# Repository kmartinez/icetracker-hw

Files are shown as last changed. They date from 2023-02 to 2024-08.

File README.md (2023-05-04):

# GDP Glacier Monitor

## Name
GDP Glacier Monitor - Hardware - part of the glacsweb.org project at The University of Southampton

## File Info
```
├── GlacTracker_PSU_V1
│   ├── GlacTracker_PSU.brd - EAGLE board file
│   ├── GlacTracker_PSU.sch - EAGLE schematic file
│   ├── GlacTracker_PSU_BOM.xlsx - Overall BOM
│   ├── mgc1g18_GlacTracker_PSU.zip - Gerber Files
│   ├── mgc1g18_GlacTracker_PSU_JLC_bom.xls - BOM for JLC pick and place
│   ├── mgc1g18_GlacTracker_PSU_top_cpl.csv - CPL for JLC pick and place
├── GlacTrackerMCU_V1 
│   ├── GlacTracker.brd - EAGLE board file
│   ├── GlacTracker.sch - EAGLE schematic file
│   ├── mgc1g18_GlacTrackerMCU.zip - Gerber Files
├── GlacTrackerMCU_V2
│   ├── GlacTracker.brd - EAGLE board file
│   ├── GlacTracker.sch - EAGLE schematic file
├── GlacTracker7 - an Eagle7 respin of the separate PSU and MCU boards into a single board
│   ├── tracker.brd - EAGLE board file
│   ├── tracker.sch - EAGLE schematic file
```

### GlacTracker3
This is in IT3 (IceTracker3) and will be the second deployed system in Iceland in 2023.
It has a simplified PSU: 3.3V and 4V with added FET switches to control power to various modules.
The GSM and SWARM are swappable and only one can be installed (to avoid issues with UARTS and we only need one)
It relies on several commercial boards: thing+, sparkfun ublox m9 GPS, sparkfun SWARM, Adafruit SD and Ardusimple's version of Xbee radio.

## GlacTracker_PSU
GlacTracker_PSU designed first to provide 3 configurable supplies through the MP2155 switching regulators. As well as a connection to the "battery" (the output of the BQ24074 Li-Ion battery Charger)
* The default settings are:
    * 3.3V
    * VCC_1 (set to 3.3V) with an optional 3.3V LDO which can be enabled by setting VCC_1 to around 4V (by changing resistor values) and connecting jumpers.
    * 5V
    * V_GSM - connection to the "battery" as described above

Each of these supplies can be enabled or disabled through both on board jumpers and via an external 6-way JST connector meaning when all supplies are disabled the leakage current is very low.

After testing it was found that using the V_GSM connector to power the GSM module was not viable as it cannot operate on voltages below 3.3V. Given this system uses Li-Ion batteries that can go as low as 2.8V, this was not a viable option.

Instead VCC_1 was set to 4V by changing R8 to 120k and two 470uF capacitors were added to the V_BAT input on the GSM module to handle current spikes during transmission. This means GSM can be used in all battery charge states.

* The current supply is setup as follows:
    * 3.3V - used to power MCU, GPS and radio. Enabled via RTC alarm enable circuit
    * VCC_1 - set to 4V used to power GSM. Enabled by MCU on demand
    * 5V - used to power SWARM. Enabled by MCU on demand
    * V_GSM - NO LONGER USED TO POWER GSM, when enabled can be used to read V_BAT

### Changes for V2
* V_GSM is now redundant as is being powered through 4V supply
* LDO is not being used to can be removed

# GlacTrackerMCU
This is the the "MCU" board with the MCU, GPS, Radio, GSM & SWARM.

The hardware is the same for a base station and rover, however the GSM & SWARM modules are not fitted on the rovers.

### GlacTrackerMCU_V2
Contains minor changes from V1 that were discovered after V1 had been "ordered":
* Capacitors added to V_BAT pin of GSM
* Diode removed from PSU_EN as not required.

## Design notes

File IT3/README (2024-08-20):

this is the final PCB design used in 2023/4

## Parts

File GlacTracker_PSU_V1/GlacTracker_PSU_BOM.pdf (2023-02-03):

Designator | Quantity Value | Footprint | Manufacture Part # | Supplier Part # | Description
C1,C6,C11 | 3 DNF | | | | SMD Capacitor
C10 | 1 22pF | 0603 | 0603CG220J500NT | JLC: C91701 | SMD Capacitor
C16,C17,C18 | 3 1uF | 0805 | 0805B105K500NT | JLC: C215803 | SMD Capacitor
C19,C20 | 2 4.7uF | 0805 | 0805X475K500CT | JLC: C296082 | SMD Capacitor
C2,C7,C12 | 3 10uF | 0805 | 0805B106K100NT | JLC: C90544 | SMD Capacitor
C3,C4,C8,C9,C13,C14 | 6 22uF | 0805 | 0805X226M100NT | JLC: C503482 | SMD Capacitor
C5,C15 | 2 68pF | 0603 | 06035A680JAT2A | JLC: C210002 | LED Red
LED1,LED2 | 2 | SML0805 | D-R080508L3-KS2 | JLC: C130114 | P-Channel 30V 5A 1.3V @ 250uA 47mΩ @ 5A,10V 2W
Q1 | 1 | TSOP-6 | AO6401A | JLC: C102604 | MOSFET N Trench 60V 4.1A 3V @ 250uA 85 mΩ @ 2.5A,10V
Q2 | 1 | SOT-89-3 | DMN6070SY-13 | JLC: C129583 | 100mW 50V ±100ppm/℃ ±1% -55℃~+155℃
R1,R4,R7 | 3 820k | 0603 | RS-03K8203FT | JLC: C322006 | 100mW Thick Film Resistors 75V ±100ppm/℃ ±1% -55℃~+155℃
R11,R13 | 2 4.7k | 0603 | 0603WAF4701T5E | JLC: C23162 | 100mW Thick Film Resistors 75V ±100ppm/℃ ±1% -55℃~+155℃
R12 | 1 1.1k | 0603 | 0603WAF1101T5E | JLC: C22764 | 100mW Thick Film Resistors 75V ±100ppm/℃ ±1% -55℃~+155℃
R14,R15 | 2 1.5k | 0603 | 0603WAF1501T5E | JLC: C22843 | 100mW Thick Film Resistors 75V ±100ppm/℃ ±1% -55℃~+155℃
R16,R17 | 2 10k | 0603 | 0603WAF1002T5E | JLC: C25804 | 100mW Thick Film Resistors 50V ±100ppm/℃ ±1% -55℃~+125℃
R2,R8 | 2 143k | 0603 | CR0603FA1433G | JLC: C100772 | 100mW Thick Film Resistors 75V ±100ppm/℃ ±1% -55℃~+155℃
R3,R9 | 2 750k | 0603 | 0603WAF7503T5E | JLC: C23240 | 100mW Thick Film Resistors 75V ±100ppm/℃ ±1% -55℃~+155℃
R5 | 1 91k | 0603 | 0603WAF9102T5E | JLC: C23265 | 100mW Thick Film Resistors 150V ±100ppm/℃ ±1% -55℃~+155℃
R6 | 1 681k | 0603 | ERJ3EKF6813V | JLC: C403328 | 100mW Thick Film Resistors 75V ±100ppm/℃ ±1% -55℃~+155℃
U1,U2,U3 | 3 MP2155GQ-Z | QFN-10_MP2155_MNP MP2155GQ-Z | JLC: C110397 | QFN-10_3x3x05P DC-DC Converter
U4 | 1 3.3V | SOT23-5 | AP2112K-3.3TRG1 | JLC: C51118 | Fixed 3.3V LDO
U5 | 1 BQ24074QFN_3X3 QFN_3X3 | BQ24074RGTR | JLC: C54313 | Battery Management IC
F1 | 1 | 1812 | MF-MSMF200-2 | RS: 647-8263 | 2A/8V PPTC Fuse
J1,J2,J3,J4,J5,J7,J8 | 7 | | S2B-PH-SM4-TB | RS: 688-1353 | JST 2MM MALE RA CONNECTOR
J6 | 1 | | SM06B-SRSS-TB | RS: 546-8827 | JST 6 pin vertical connector
L1,L2,L3 | 3 | 7050 | 744314330 | RS: 736-1951 | Shielded Wire-wound SMD Inductor

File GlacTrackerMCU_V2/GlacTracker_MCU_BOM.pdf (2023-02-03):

Designator | Quantity | Value | Footprint | Description
BT1 | | 3000TR | BAT_3000TR | Ultra Low Profile SMT Coin Cell Battery Contact Retainer for 12 mm Cell
C1, C2, C3, C4, C6, C8 | | 100n | 0603 | Capacitor - Generic
C5 | | 1uF | 0603 | Capacitor - Generic
C7 | | 100pf | 0603 | Capacitor - Generic
C9, C10 | | 470uF | TH | Capacitor Polarised - Generic
J1 | SPARKFUN-SAMD51-THINGPLUS TH
J2, J3, J4 | | | JST-2-SMD | JST 2MM MALE RA CONNECTOR
J5 | JST_6_PIN_VERTICAL | JST-6-SMD-VERT-1.0MM JST 6 pin vertical connector
LED1, LED2, LED3 | | | CHIP-LED0805 | LED
Q1 | | 2N3906 | TO92 | PNP Transistor
R1, R2 | | 100k | 0603 | Generic Resistor Package
R3, R4, R5 | | 1k | 0603 | Generic Resistor Package
U1 | | DS3231-BREAKOUT | TH
U2 | | FONA-800-BREAKOUT | TH
U4 | | SPARKFUN-SWARM-M138 | TH
U5 | | SPARKFUN-GPS-ZED-F9P | TH
XB1 | | XBEE-SX868 | TH | XBee(TM)/XBee-PRO(TM) ZB SMT RF Modules.

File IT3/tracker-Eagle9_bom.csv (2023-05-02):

Comment | Designator | Footprint | LCSC Part #
 | 3.3V | CHIP-LED0805 | C142303
 | 4.4V | CHIP-LED0805 | C142303
 | GPS | CHIP-LED0805 | C142303
 | GSM | CHIP-LED0805 | C142303
 | JP1 | JP1
 | JP2 | JP1
 | JP3 | JP1
 | JP5 | JP1
 | LED_EN | JP1
 | LED4 | SML0805 | C142303
 | LED5 | SML0805 | C142303
820k | R6 | 0603
845k | R9 | 0603
1.1k | R14 | 0603
1.5k | R16 R17 | 0603
1k | R3 R4 R5 R27 | 0603
1uF | C21 | C0805
1uF | C5 | CAPC1608X85 | C105524
1uF | C23 | CAPC2012X110 | C318694
2A/16V | F1 | F1812 | C70126
2N3906 | Q1 | TO92
3.3uH | L1 L3 | WE-HCI_7050
4.7k | R13 R15 | 0603
4.7uF | C24 C25 | CAPC2012X110 | C730468
10k | R23 R28 | 0603
10uF | C12 C17 | CAPC2012X110 | C162430
22-23-2021 | SOLAR | 22-23-2021
22uF | C13 C14 C18 C19 | CAPC2012X110 | C77074
68pF | C15 C20 | CAPC1608X85 | C779986
100k | R1 R2 R18 R19 R20 R21 R22 | 0603
100n | C1 C2 C3 C4 C6 C8 | CAPC1608X85 | C913910
100pf | C7 | CAPC1608X85 | C307357
143k | R7 | 0603
121k | R10 | 0603
340K 0.1% | R25 | R0805 | C865414
470uF | C9 C10 | CAPPRD508W65D1000H1100B
680K 0.1% | R24 | R0805 | C445667
750k | R8 R11 | 0603
3000TR | BT1 | BAT_3000TR | C964830
ADAFRUIT-XTSD | U$1 | ADAFRUIT-XTSD
ADXL343BCCZ-RL7 | U1 | PQFN80P300X500X100-14N
BQ24074QFN_3X3 | U8 | QFN_3X3 | C54313
DMG6602SVT | Q2 Q3 Q7 | TSOT26 | C110497
DNF | C11 C16 | CAPC2012X110
DNF | R12 | P640
DNP | R26 | 0603
DS3231SN | U7 | SOIC127P1032X265-16N
FONA-800-BREAKOUTNOHOLE | U2 | FONA-800-BREAKOUT-NH
JUMPER-SMT_2_NC_TRACE_SILK | JP4 JP10 | SMT-JUMPER_2_NC_TRACE_SILK
MMBT3906LT1SMD | Q6 | SOT23-BEC | C53444
MP2155GQ-Z | U3 U6 | QFN-10_MP2155_MNP
SLOT130.5 | U$2 | SLOT130.5
SPARKFUN-GPS-ZED-F9P | U5 | SPARKFUN-GPS-ZED-F9P
SPARKFUN-SWARM-M138NOTOPHOLE | U4 | SPARKFUN-SWARM-M138-NTH
TEST-POINTTP_15TH_THRU | TP1 TP3 TP6 | TP_15TH
THING_PLUS_PHYSICAL | J1 | THING_PLUS
XBEE-PRO | XB1 | XBEE-PRO
XT30PW-M | BAT | XT30PW-M

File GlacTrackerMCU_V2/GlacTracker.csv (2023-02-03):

Part | Value | Device | Package | Description | AVAILABILITY | CATEGORY | DESCRIPTION | MANUFACTURER | MF | MP | MPN | OPERATING_TEMP | PACKAGE | PART_STATUS | POPULARITY | PRICE | PROD_ID | PURCHASE-URL | ROHS_COMPLIANT | SERIES | SF_ID | SUB-CATEGORY | THERMALLOSS | TP_SIGNAL_NAME | TYPE | VALUE | VOLTAGE_RATING
BT1 | 3000TR | 3000TR | BAT_3000TR | Ultra Low Profile SMT Coin Cell Battery Contact Retainer for 12 mm Cell Check availability | In Stock |  | SMT Holder for 12mm Cell-Tin Nickel Plate on T&R |  | Keystone | 3000TR |  |  | None |  |  | None |  | https://pricing.snapeda.com/search/part/3000TR/?ref=eda
C1 | 100n | C_CHIP-0603(1608-METRIC) | CAPC1608X85 | Capacitor - Generic |  | Capacitor
C2 | 100n | C_CHIP-0603(1608-METRIC) | CAPC1608X85 | Capacitor - Generic |  | Capacitor
C3 | 100n | C_CHIP-0603(1608-METRIC) | CAPC1608X85 | Capacitor - Generic |  | Capacitor
C4 | 100n | C_CHIP-0603(1608-METRIC) | CAPC1608X85 | Capacitor - Generic |  | Capacitor
C5 | 1uF | C_CHIP-0603(1608-METRIC) | CAPC1608X85 | Capacitor - Generic |  | Capacitor
C6 | 100n | C_CHIP-0603(1608-METRIC) | CAPC1608X85 | Capacitor - Generic |  | Capacitor
C7 | 100pf | C_CHIP-0603(1608-METRIC) | CAPC1608X85 | Capacitor - Generic |  | Capacitor
C8 | 100n | C_CHIP-0603(1608-METRIC) | CAPC1608X85 | Capacitor - Generic |  | Capacitor
C9 | 470uF | C-POL_RADIAL-11MM-DIA | CAPPRD508W65D1000H1100B | Capacitor Polarised - Generic |  | Capacitor
C10 | 470uF | C-POL_RADIAL-11MM-DIA | CAPPRD508W65D1000H1100B | Capacitor Polarised - Generic |  | Capacitor
J1 | THING_PLUS_PHYSICAL | THING_PLUS_PHYSICAL | THING_PLUS
J2 |  | JST_2MM_MALE | JST-2-SMD | JST 2MM MALE RA CONNECTOR |  |  |  |  |  |  |  |  |  |  |  |  | CONN-11443 |  |  |  | PRT-08612
J3 |  | JST_2MM_MALE | JST-2-SMD | JST 2MM MALE RA CONNECTOR |  |  |  |  |  |  |  |  |  |  |  |  | CONN-11443 |  |  |  | PRT-08612
J4 |  | JST_2MM_MALE | JST-2-SMD | JST 2MM MALE RA CONNECTOR |  |  |  |  |  |  |  |  |  |  |  |  | CONN-11443 |  |  |  | PRT-08612
J5 | JST_6_PIN_VERTICAL | JST_6_PIN_VERTICAL | JST-6-SMD-VERT-1.0MM | JST 6 pin vertical connector |  |  |  |  |  |  |  |  |  |  |  |  | CONN-08249 |  |  |  | GPS-00579
JP1 | JUMPER-SMT_2_NC_TRACE_SILK | JUMPER-SMT_2_NC_TRACE_SILK | SMT-JUMPER_2_NC_TRACE_SILK | Normally closed trace jumper
JP2 | JUMPER-SMT_2_NC_TRACE_SILK | JUMPER-SMT_2_NC_TRACE_SILK | SMT-JUMPER_2_NC_TRACE_SILK | Normally closed trace jumper
JP3 | JUMPER-SMT_2_NC_TRACE_SILK | JUMPER-SMT_2_NC_TRACE_SILK | SMT-JUMPER_2_NC_TRACE_SILK | Normally closed trace jumper
LED1 |  | LEDCHIP-LED0805 | CHIP-LED0805 | LED |  |  |  |  |  |  |  |  |  |  | 68
LED2 |  | LEDCHIP-LED0805 | CHIP-LED0805 | LED |  |  |  |  |  |  |  |  |  |  | 68
LED3 |  | LEDCHIP-LED0805 | CHIP-LED0805 | LED |  |  |  |  |  |  |  |  |  |  | 68
Q1 | 2N3906 | 2N3906 | TO92 | PNP Transistor |  |  |  |  |  |  |  |  |  |  | 11
R1 | 100k | RESISTOR0603 | 0603 | Generic Resistor Package
R2 | 100k | RESISTOR0603 | 0603 | Generic Resistor Package
R3 | 1k | RESISTOR0603 | 0603 | Generic Resistor Package
R4 | 1k | RESISTOR0603 | 0603 | Generic Resistor Package
R5 | 1k | RESISTOR0603 | 0603 | Generic Resistor Package
TP1 | TP2P2-38-17 | TP2P2-38-17 | P2-38-17 | Test pad |  |  |  |  |  |  |  |  |  |  | 0
TP2 | TP2P2-38-17 | TP2P2-38-17 | P2-38-17 | Test pad |  |  |  |  |  |  |  |  |  |  | 0
TP3 | TP2P2-38-17 | TP2P2-38-17 | P2-38-17 | Test pad |  |  |  |  |  |  |  |  |  |  | 0
U1 | DS3231-BREAKOUT | DS3231-BREAKOUT | DS3231-BREAKOUT
U2 | FONA-800-BREAKOUT | FONA-800-BREAKOUT | FONA-800-BREAKOUT
U4 | SPARKFUN-SWARM-M138 | SPARKFUN-SWARM-M138 | SPARKFUN-SWARM-M138
U5 | SPARKFUN-GPS-ZED-F9P | SPARKFUN-GPS-ZED-F9P | SPARKFUN-GPS-ZED-F9P
XB1 | XBEE-SMT | XBEE-SMT | XBEE-SMT | XBee(TM)/XBee-PRO(TM) ZB SMT RF Modules.

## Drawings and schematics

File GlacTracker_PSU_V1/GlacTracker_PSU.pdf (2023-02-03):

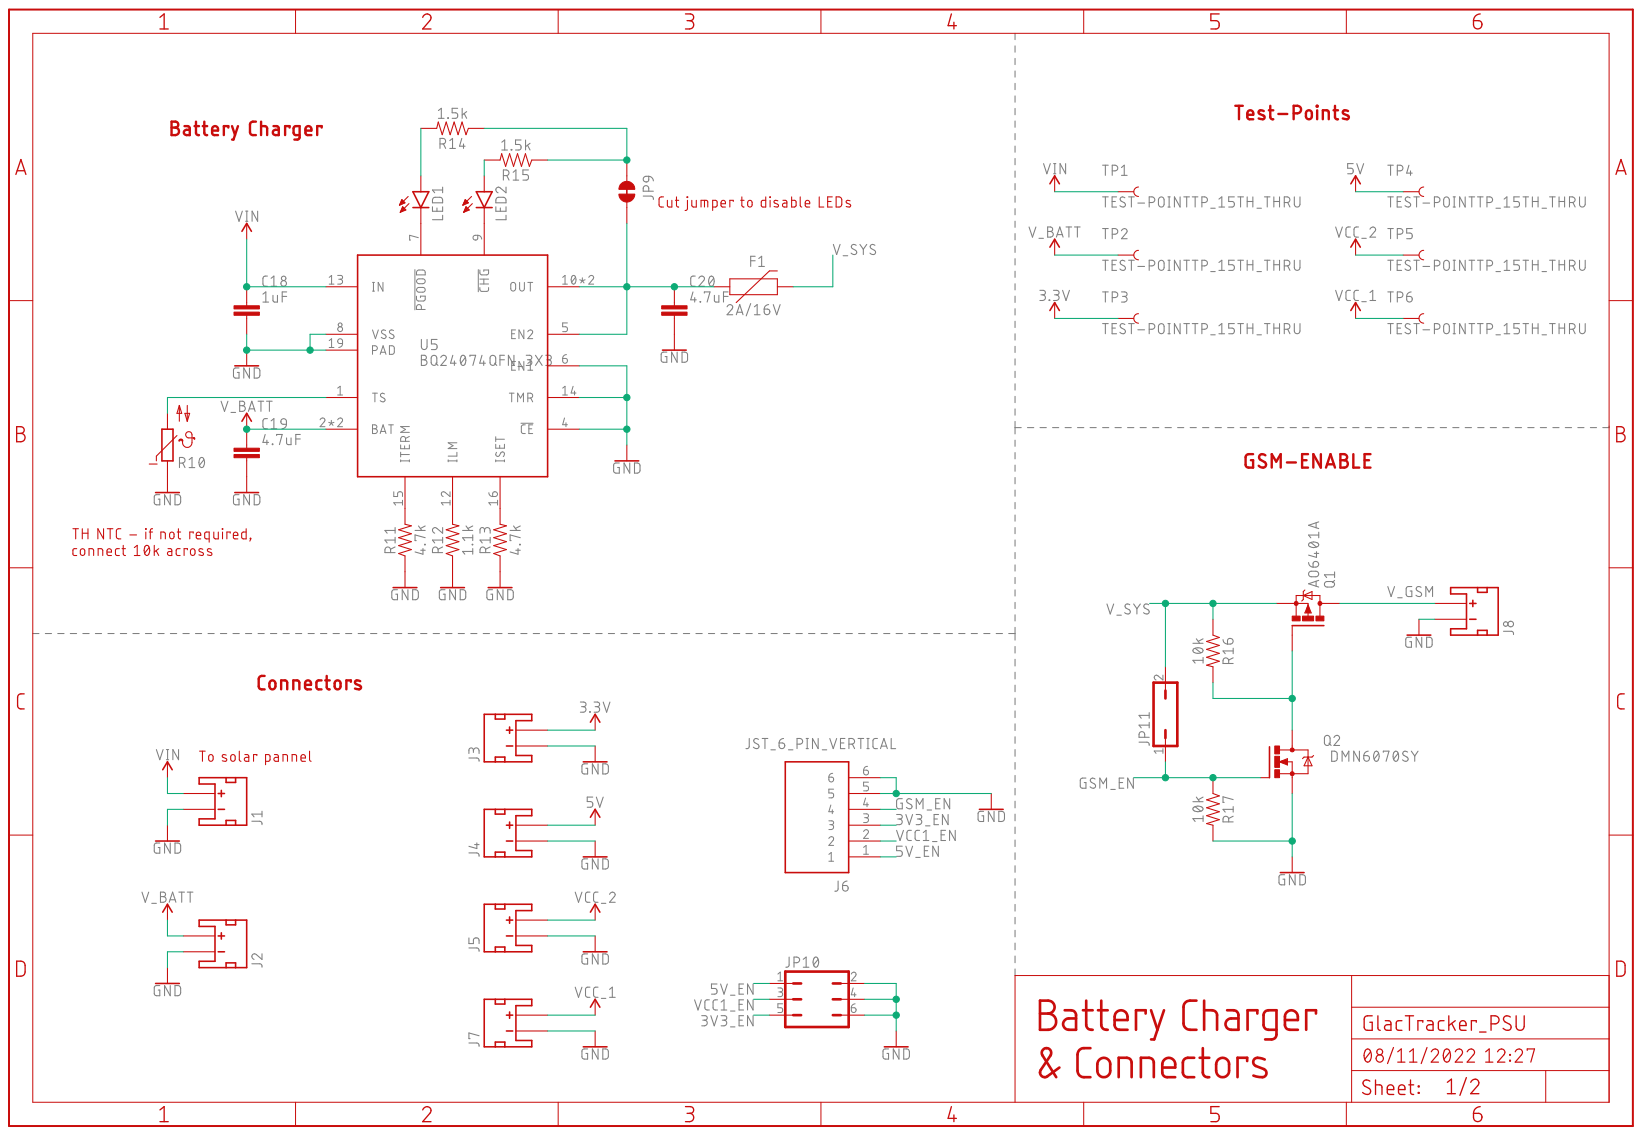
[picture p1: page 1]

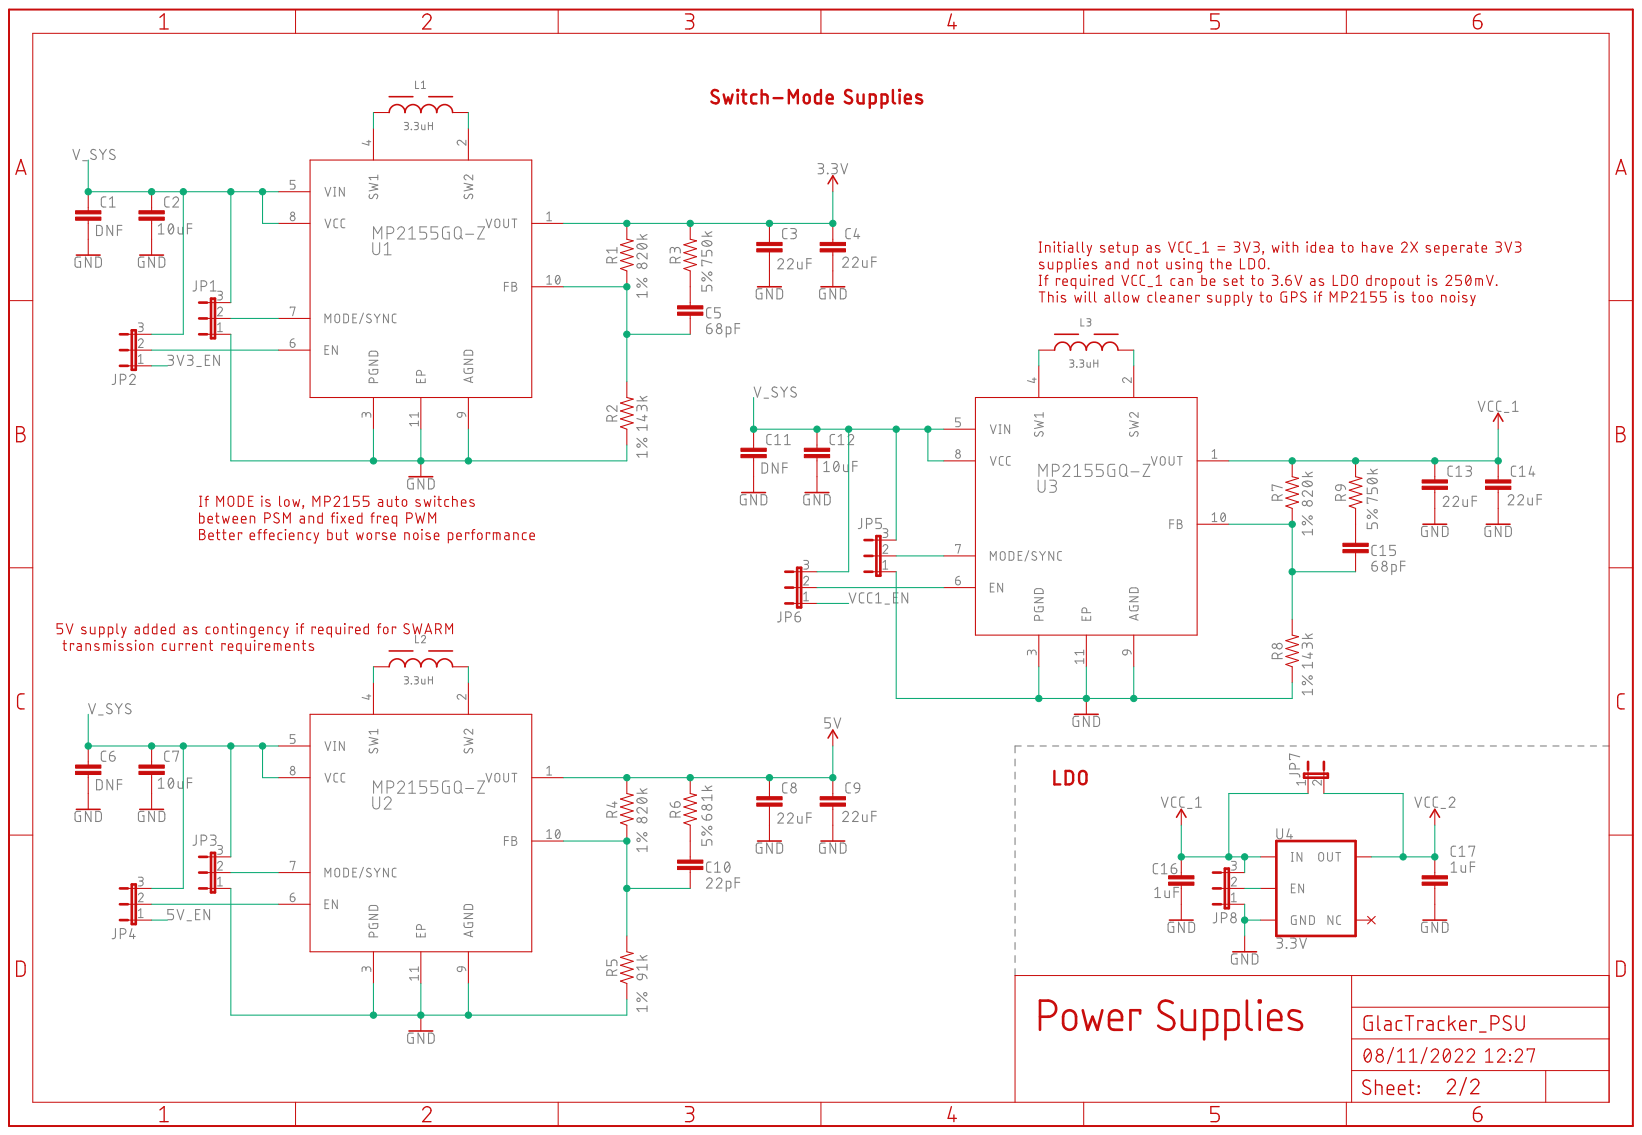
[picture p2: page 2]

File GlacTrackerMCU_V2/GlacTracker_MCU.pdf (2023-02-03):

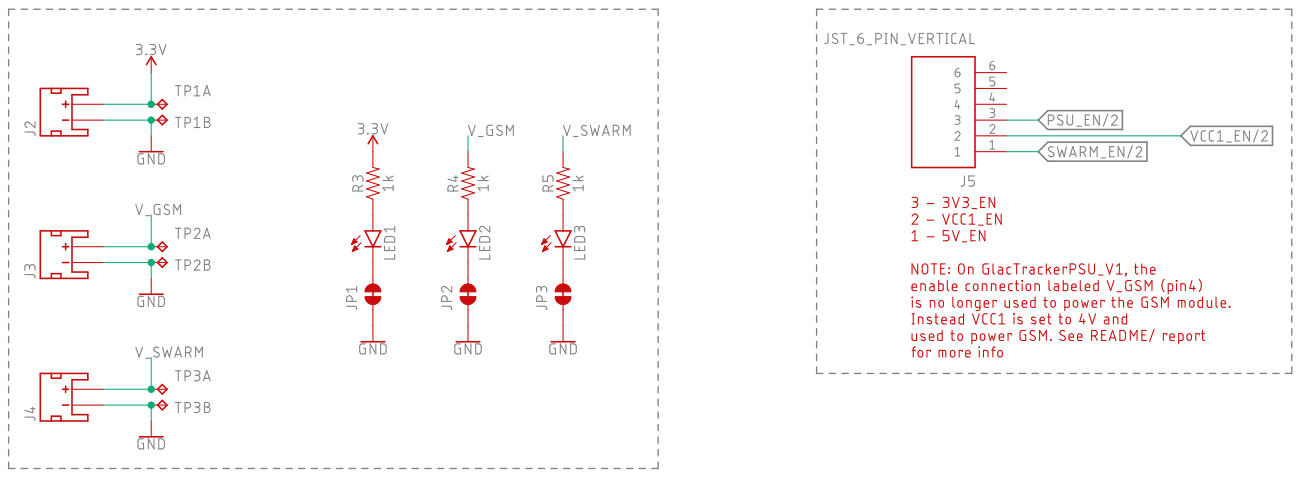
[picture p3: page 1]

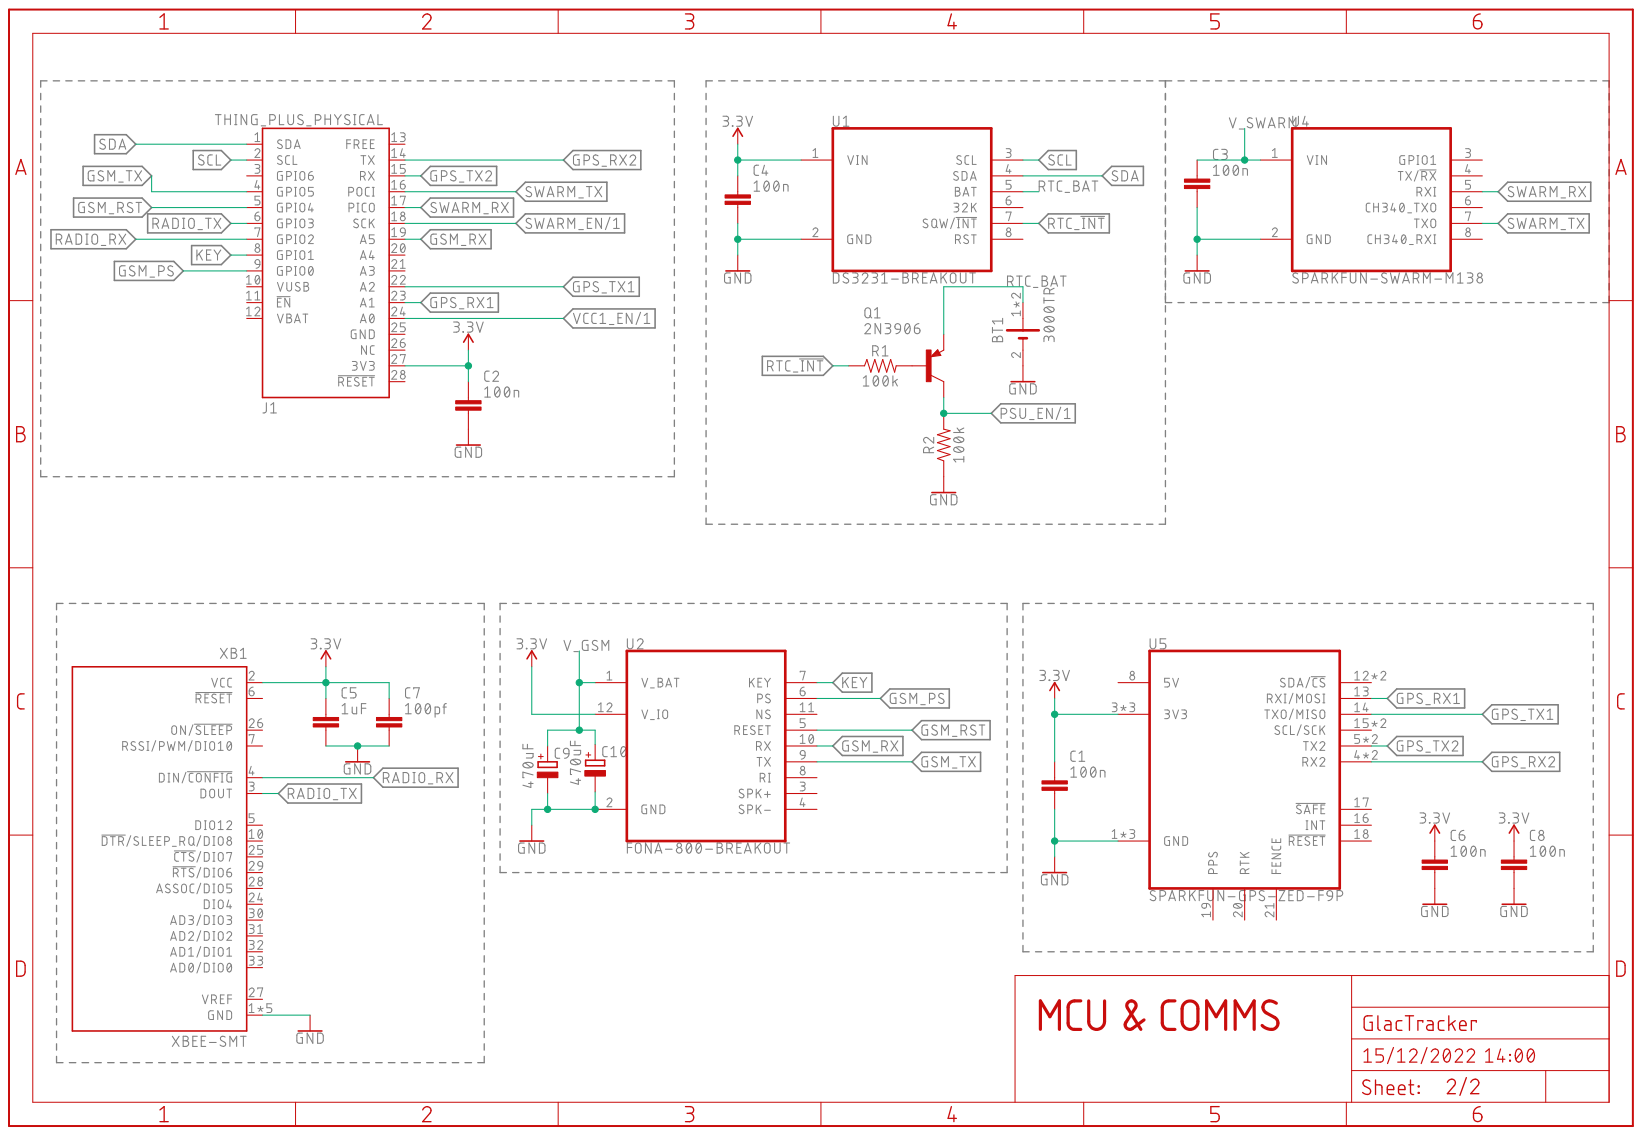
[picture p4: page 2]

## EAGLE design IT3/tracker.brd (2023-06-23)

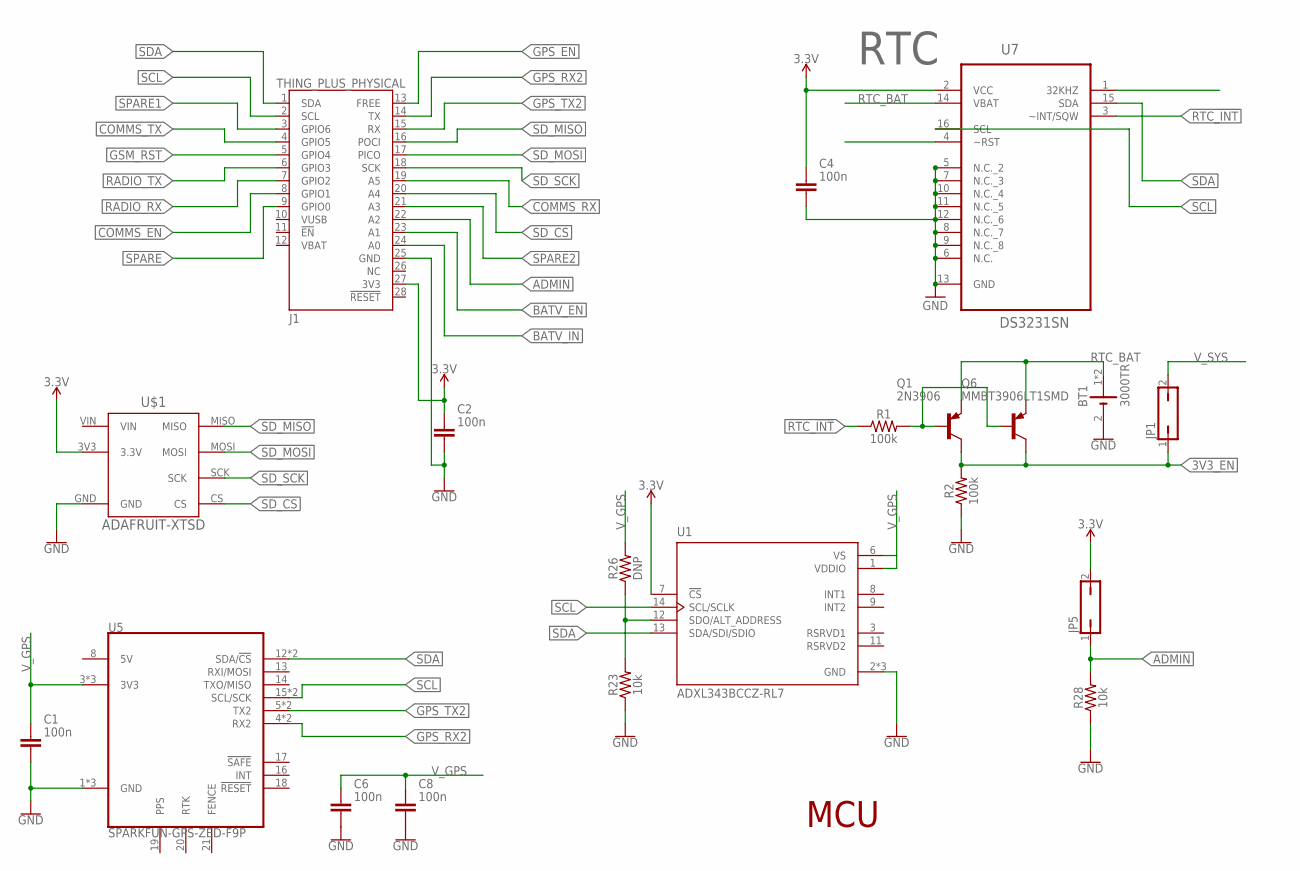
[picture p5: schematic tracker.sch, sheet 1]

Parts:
BT1: 3000TR; BAT_3000TR
C1, C2, C4, C6, C8: 100n; CAPC1608X85
J1: THING_PLUS_PHYSICAL; THING_PLUS
JP1, JP5: JP1Q; JP1
Q1: 2N3906; TO92
Q6: MMBT3906LT1SMD; SOT23-BEC
R1, R2: 100k; 0603
R23, R28: 10k; 0603
R26: DNP; 0603
U1: ADXL343BCCZ-RL7; PQFN80P300X500X100-14N
U5: SPARKFUN-GPS-ZED-F9P
U7: DS3231SN; SOIC127P1032X265-16N
U$1: ADAFRUIT-XTSD

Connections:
3.3V: C2.1, C4.1, J1.27 (3V3), JP5.2, U1.7 (!CS), U7.2 (VCC), U$1.3V3 (3.3V); also elsewhere on the board
3V3_EN: JP1.1, Q1.1 (C), Q6.C, R2.2; also elsewhere on the board
ADMIN: J1.22 (A2), JP5.1, R28.2
BATV_EN: J1.23 (A1); also elsewhere on the board
BATV_IN: J1.24 (A0); also elsewhere on the board
COMMS_EN: J1.8 (GPIO1); also elsewhere on the board
COMMS_RX: J1.19 (A5); also elsewhere on the board
COMMS_TX: J1.4 (GPIO5); also elsewhere on the board
GND: BT1.2 (-), C1.2, C2.2, C4.2, C6.2, C8.2, J1.25 (GND), R2.1, R23.1, R28.1, U1.2 (GND), U1.4 (GND), U1.5 (GND), U5.1 (GND), U5.7 (GND), U5.25 (GND), U7.5 (N.C._2), U7.6 (N.C.), U7.7 (N.C._3), U7.8 (N.C._7), U7.9 (N.C._8), U7.10 (N.C._4), U7.11 (N.C._5), U7.12 (N.C._6), U7.13 (GND), U$1.GND; also elsewhere on the board
GPS_EN: J1.13 (FREE); also elsewhere on the board
GPS_RX2: J1.14 (TX), U5.4 (RX2), U5.11 (RX2)
GPS_TX2: J1.15 (RX), U5.5 (TX2), U5.10 (TX2)
GSM_RST: J1.5 (GPIO4); also elsewhere on the board
unnamed: R23.2, R26.1, U1.12 (SDO/ALT_ADDRESS)
unnamed: Q1.2 (B), Q6.B, R1.2
RADIO_RX: J1.7 (GPIO2); also elsewhere on the board
RADIO_TX: J1.6 (GPIO3); also elsewhere on the board
RTC_!INT: R1.1, U7.3 (~INT/SQW)
RTC_BAT: BT1.1 (+), BT1.3 (+), Q1.3 (E), Q6.E, U7.14 (VBAT)
SCL: J1.2 (SCL), U1.14 (SCL/SCLK), U5.15 (SCL/SCK), U5.22 (SCL/SCK), U7.16 (SCL)
SDA: J1.1 (SDA), U1.13 (SDA/SDI/SDIO), U5.12 (SDA/!CS), U5.23 (SDA/!CS), U7.15 (SDA)
SD_CS: J1.20 (A4), U$1.CS
SD_MISO: J1.16 (POCI), U$1.MISO
SD_MOSI: J1.17 (PICO), U$1.MOSI
SD_SCK: J1.18 (SCK), U$1.SCK
SPARE: J1.9 (GPIO0)
SPARE1: J1.3 (GPIO6)
SPARE2: J1.21 (A3)
V_GPS: C1.1, C6.1, C8.1, R26.2, U1.1 (VDDIO), U1.6 (VS), U5.3 (3V3), U5.9 (3V3), U5.24 (3V3); also elsewhere on the board
V_SYS: JP1.2; also elsewhere on the board

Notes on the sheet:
MCU
RTC

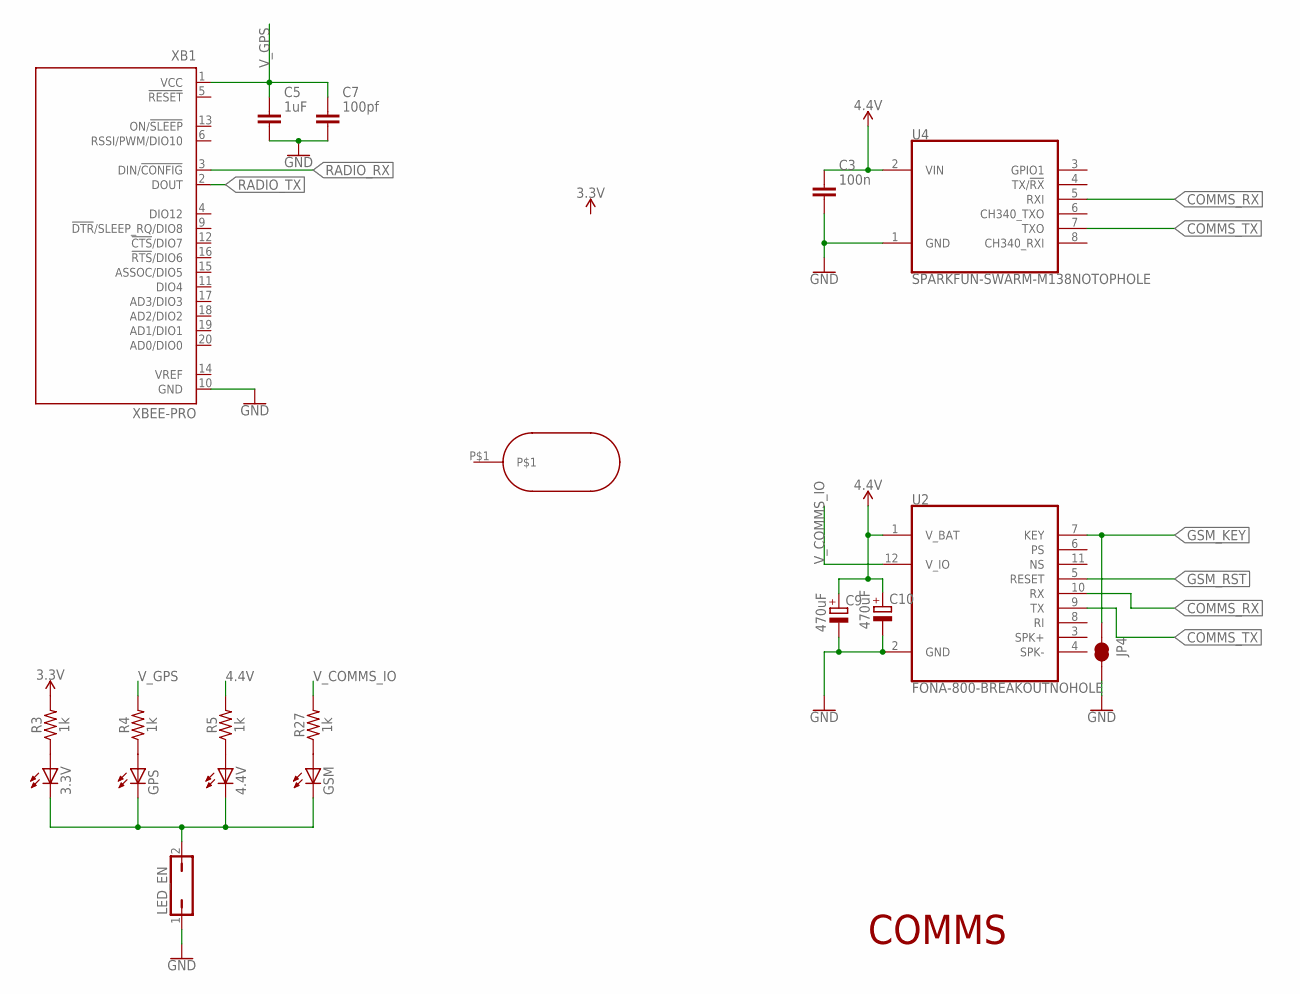
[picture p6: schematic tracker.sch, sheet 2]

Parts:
3.3V, 4.4V: LEDCHIP-LED0805; CHIP-LED0805
C3: 100n; CAPC1608X85
C5: 1uF; CAPC1608X85
C7: 100pf; CAPC1608X85
C9, C10: 470uF; CAPPRD508W65D1000H1100B
GPS: LEDCHIP-LED0805; CHIP-LED0805
GSM: LEDCHIP-LED0805; CHIP-LED0805
JP4: JUMPER-SMT_2_NC_TRACE_SILK; SMT-JUMPER_2_NC_TRACE_SILK
LED_EN: JP1Q; JP1
R3, R4, R5, R27: 1k; 0603
U2: FONA-800-BREAKOUTNOHOLE; FONA-800-BREAKOUT-NH
U4: SPARKFUN-SWARM-M138NOTOPHOLE; SPARKFUN-SWARM-M138-NTH
U$2: SLOT130.5
XB1: XBEE-PRO

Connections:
3.3V: R3.2; also elsewhere on the board
4.4V: C3.1, C9.1 (+), C10.1 (+), R5.2, U2.1 (V_BAT), U4.2 (VIN); also elsewhere on the board
COMMS_RX: U2.10 (RX), U4.5 (RXI); also elsewhere on the board
COMMS_TX: U2.9 (TX), U4.7 (TXO); also elsewhere on the board
GND: C3.2, C5.2, C7.2, C9.2 (-), C10.2 (-), JP4.2, LED_EN.1, U2.2 (GND), U4.1 (GND), XB1.10 (GND); also elsewhere on the board
GSM_KEY: JP4.1, U2.7 (KEY)
GSM_RST: U2.5 (RESET); also elsewhere on the board
unnamed: 3.3V.C, 4.4V.C, GPS.C, GSM.C, LED_EN.2
unnamed: GPS.A, R4.1
unnamed: 3.3V.A, R3.1
unnamed: GSM.A, R27.1
unnamed: 4.4V.A, R5.1
RADIO_RX: XB1.3 (DIN/!CONFIG); also elsewhere on the board
RADIO_TX: XB1.2 (DOUT); also elsewhere on the board
V_COMMS_IO: R27.2, U2.12 (V_IO); also elsewhere on the board
V_GPS: C5.1, C7.1, R4.2, XB1.1 (VCC); also elsewhere on the board

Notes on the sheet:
COMMS

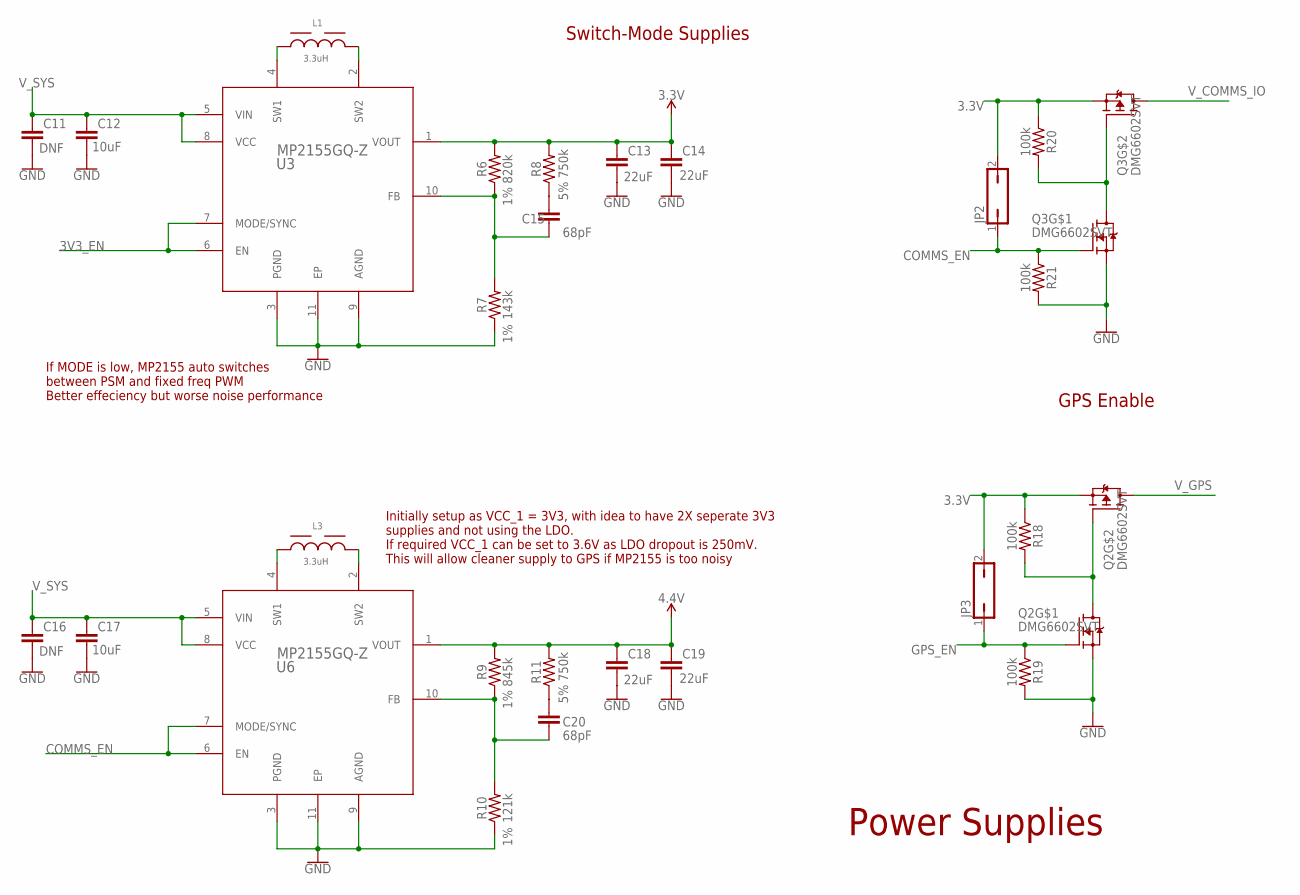
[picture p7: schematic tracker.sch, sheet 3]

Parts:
C11, C16: DNF; CAPC2012X110
C12, C17: 10uF; CAPC2012X110; VOLTAGE_RATING 6.3V
C13, C14, C18, C19: 22uF; CAPC2012X110; VOLTAGE_RATING 10V
C15, C20: 68pF; CAPC1608X85; VOLTAGE_RATING 50V
JP2, JP3: JP1Q; JP1
L1, L3: 3.3uH; WE-HCI_7050
Q2, Q3: DMG6602SVT; TSOT26
R6: 820k; 0603; TOLERANCE 1%
R7: 143k; 0603; TOLERANCE 1%
R8, R11: 750k; 0603; TOLERANCE 5%
R9: 845k; 0603; TOLERANCE 1%
R10: 121k; 0603; TOLERANCE 1%
R18, R19, R20, R21: 100k; 0603
U3, U6: MP2155GQ-Z; QFN-10_MP2155_MNP

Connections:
3.3V: C13.1, C14.1, JP2.2, JP3.2, Q2.P$2 (S), Q3.P$2 (S), R6.2, R8.2, R18.1, R20.1, U3.1 (VOUT); also elsewhere on the board
3V3_EN: U3.6 (EN), U3.7 (MODE/SYNC); also elsewhere on the board
4.4V: C18.1, C19.1, R9.2, R11.2, U6.1 (VOUT); also elsewhere on the board
COMMS_EN: JP2.1, Q3.P$1 (G), R21.1, U6.6 (EN), U6.7 (MODE/SYNC); also elsewhere on the board
GND: C11.2, C12.2, C13.2, C14.2, C16.2, C17.2, C18.2, C19.2, Q2.P$5 (S), Q3.P$5 (S), R7.1, R10.1, R19.2, R21.2, U3.3 (PGND), U3.9 (AGND), U3.11 (EP), U6.3 (PGND), U6.9 (AGND), U6.11 (EP); also elsewhere on the board
GPS_EN: JP3.1, Q2.P$1 (G), R19.1; also elsewhere on the board
unnamed: C15.2, R6.1, R7.2, U3.10 (FB)
unnamed: C15.1, R8.1
unnamed: L1.1, U3.4 (SW1)
unnamed: L1.2, U3.2 (SW2)
unnamed: C20.2, R9.1, R10.2, U6.10 (FB)
unnamed: C20.1, R11.1
unnamed: L3.1, U6.4 (SW1)
unnamed: L3.2, U6.2 (SW2)
unnamed: Q2.P$3 (G), Q2.P$6 (D), R18.2
unnamed: Q3.P$3 (G), Q3.P$6 (D), R20.2
V_COMMS_IO: Q3.P$4 (D); also elsewhere on the board
V_GPS: Q2.P$4 (D); also elsewhere on the board
V_SYS: C11.1, C12.1, C16.1, C17.1, U3.5 (VIN), U3.8 (VCC), U6.5 (VIN), U6.8 (VCC); also elsewhere on the board

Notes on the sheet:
Initially setup as VCC_1 = 3V3, with idea to have 2X seperate 3V3 supplies and not using the LDO. If required VCC_1 can be set to 3.6V as LDO dropout is 250mV. This will allow cleaner supply to GPS if MP2155 is too noisy
Power Supplies
If MODE is low, MP2155 auto switches between PSM and fixed freq PWM Better effeciency but worse noise performance
Switch-Mode Supplies
GPS Enable

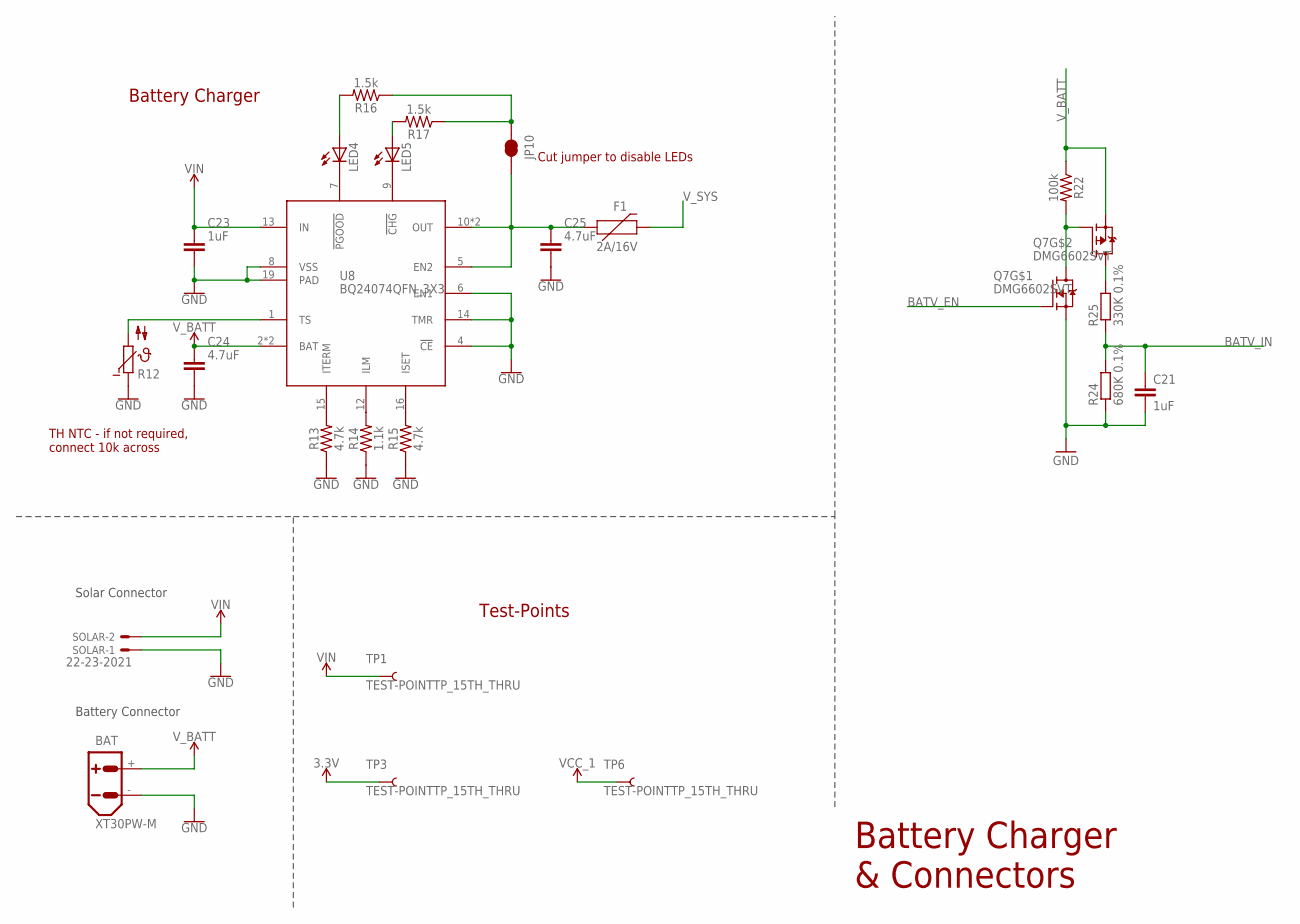
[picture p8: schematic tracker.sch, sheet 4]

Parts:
BAT: XT30PW-M
C21: 1uF; C0805
C23: 1uF; CAPC2012X110
C24, C25: 4.7uF; CAPC2012X110
F1: 2A/16V; F1812
JP10: JUMPER-SMT_2_NC_TRACE_SILK; SMT-JUMPER_2_NC_TRACE_SILK
LED4, LED5: LEDSML0805; SML0805
Q7: DMG6602SVT; TSOT26
R12: DNF; P640
R13, R15: 4.7k; 0603
R14: 1.1k; 0603
R16, R17: 1.5k; 0603
R22: 100k; 0603
R24: 680K 0.1%; R0805
R25: 330K 0.1%; R0805
SOLAR: 22-23-2021
TP1, TP3, TP6: TEST-POINTTP_15TH_THRU; TP_15TH
U8: BQ24074QFN_3X3; QFN_3X3

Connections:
3.3V: TP3.P$1; also elsewhere on the board
4.4V: TP6.P$1; also elsewhere on the board
BATV_EN: Q7.P$1 (G); also elsewhere on the board
BATV_IN: C21.1, R24.2, R25.1; also elsewhere on the board
GND: BAT.-, C21.2, C23.2, C24.2, C25.2, Q7.P$5 (S), R12.1, R13.1, R14.1, R15.1, R24.1, SOLAR.1, U8.4 (!CE), U8.6 (EN1), U8.8 (VSS), U8.14 (TMR), U8.19 (PAD); also elsewhere on the board
unnamed: Q7.P$3 (G), Q7.P$6 (D), R22.2
unnamed: R12.2, U8.1 (TS)
unnamed: R13.2, U8.15 (ITERM)
unnamed: R14.2, U8.12 (ILM)
unnamed: R15.2, U8.16 (ISET)
unnamed: LED4.C, U8.7 (!PGOOD)
unnamed: LED5.C, U8.9 (!CHG)
unnamed: JP10.1, R16.1, R17.1
unnamed: LED4.A, R16.2
unnamed: LED5.A, R17.2
unnamed: C25.1, F1.1, JP10.2, U8.5 (EN2), U8.10 (OUT), U8.11 (OUT)
VCC_HP2_SW1: Q7.P$4 (D), R25.2
VIN: C23.1, SOLAR.2, TP1.P$1, U8.13 (IN)
V_BATT: BAT.+, C24.1, Q7.P$2 (S), R22.1, U8.2 (BAT), U8.3 (BAT)
V_SYS: F1.2; also elsewhere on the board

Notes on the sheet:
TH NTC - if not required, connect 10k across
Battery Charger & Connectors
Cut jumper to disable LEDs
Battery Charger
Test-Points
Battery Connector
Solar Connector

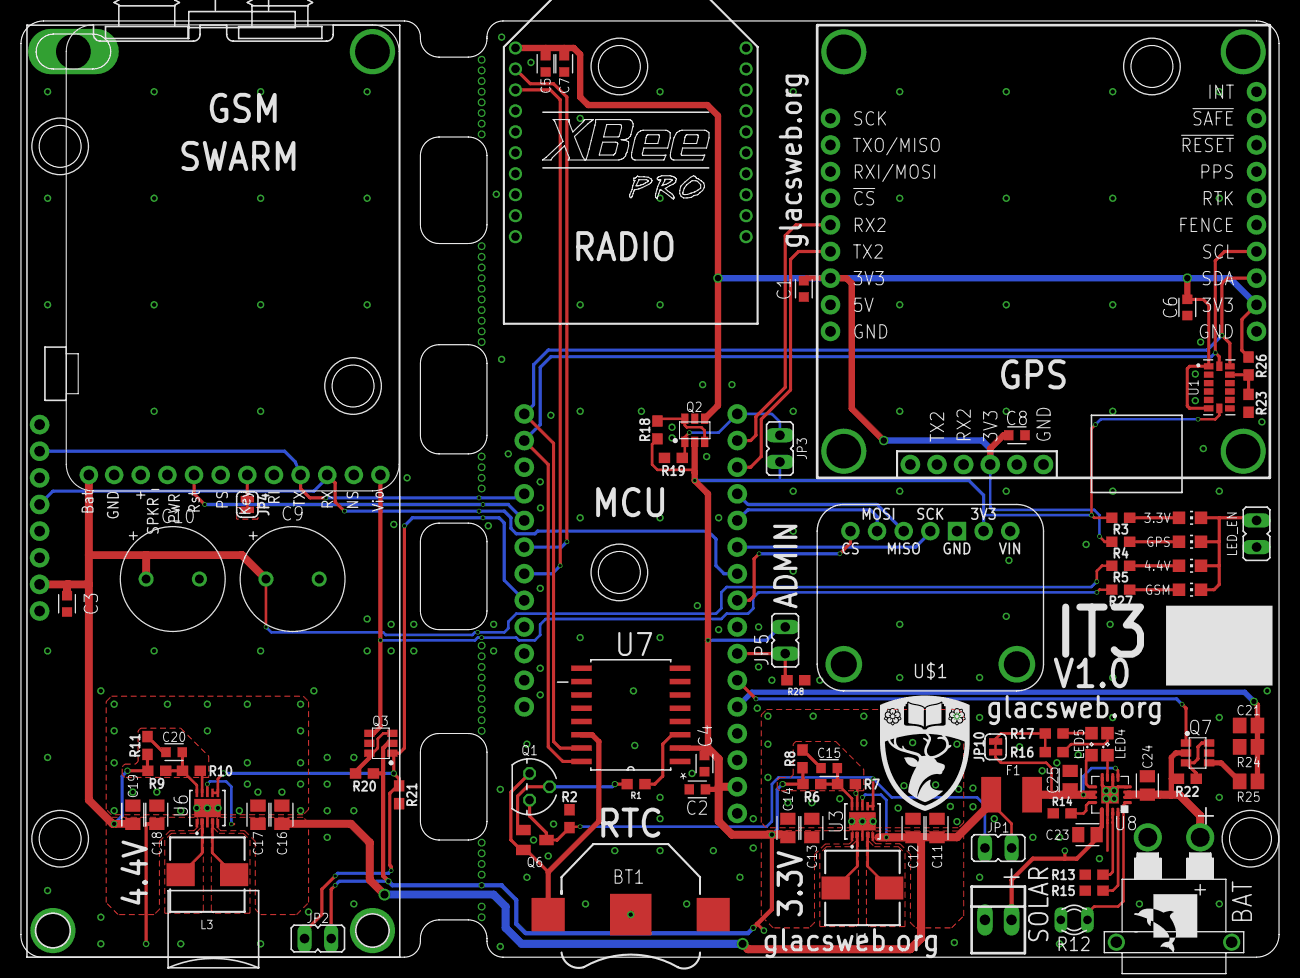
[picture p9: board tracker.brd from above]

Board: 2 copper layers, 120.0 x 89.3 mm, 91 parts (0 on the bottom side), 59 nets.

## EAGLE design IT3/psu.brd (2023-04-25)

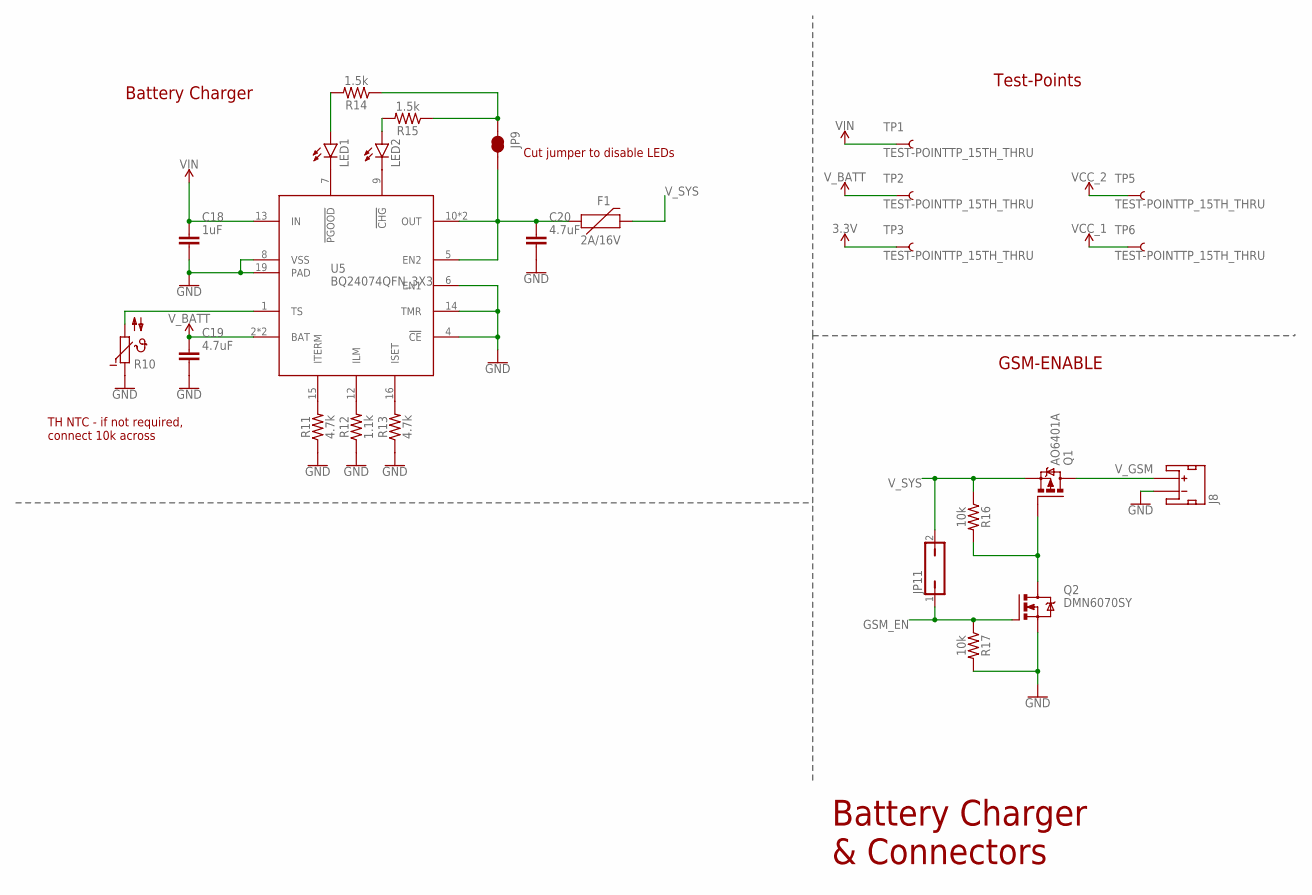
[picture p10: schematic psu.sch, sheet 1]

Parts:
C18: 1uF; CAPC2012X110
C19, C20: 4.7uF; CAPC2012X110
F1: 2A/16V; F1812
J8: JST_2MM_MALE; JST-2-SMD
JP9: JUMPER-SMT_2_NC_TRACE_SILK; SMT-JUMPER_2_NC_TRACE_SILK
JP11: JP1Q; JP1
LED1, LED2: LEDSML0805; SML0805
Q1: AO6401A; TSOP-6
Q2: DMN6070SY; SOT-89-3
R10: DNF; P640
R11, R13: 4.7k; 0603
R12: 1.1k; 0603
R14, R15: 1.5k; 0603
R16, R17: 10k; 0603
TP1, TP2, TP3, TP5, TP6: TEST-POINTTP_15TH_THRU; TP_15TH
U5: BQ24074QFN_3X3; QFN_3X3

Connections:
3.3V: TP3.P$1; also elsewhere on the board
GND: C18.2, C19.2, C20.2, J8.1 (-), Q2.3 (S), R10.1, R11.1, R12.1, R13.1, R17.2, U5.4 (!CE), U5.6 (EN1), U5.8 (VSS), U5.14 (TMR), U5.19 (PAD); also elsewhere on the board
GSM_EN: JP11.1, Q2.1 (G), R17.1
unnamed: R10.2, U5.1 (TS)
unnamed: R11.2, U5.15 (ITERM)
unnamed: R12.2, U5.12 (ILM)
unnamed: R13.2, U5.16 (ISET)
unnamed: LED1.C, U5.7 (!PGOOD)
unnamed: LED2.C, U5.9 (!CHG)
unnamed: JP9.1, R14.1, R15.1
unnamed: LED1.A, R14.2
unnamed: LED2.A, R15.2
unnamed: C20.1, F1.1, JP9.2, U5.5 (EN2), U5.10 (OUT), U5.11 (OUT)
unnamed: Q1.3 (G), Q2.2 (D), Q2.4 (D), R16.2
VCC_1: TP6.P$1; also elsewhere on the board
VCC_2: TP5.P$1; also elsewhere on the board
VIN: C18.1, TP1.P$1, U5.13 (IN)
V_BATT: C19.1, TP2.P$1, U5.2 (BAT), U5.3 (BAT)
V_GSM: J8.2 (+), Q1.1 (D), Q1.2 (D), Q1.5 (D), Q1.6 (D)
V_SYS: F1.2, JP11.2, Q1.4 (S), R16.1; also elsewhere on the board

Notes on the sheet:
TH NTC - if not required, connect 10k across
Battery Charger & Connectors
Cut jumper to disable LEDs
Battery Charger
Test-Points
GSM-ENABLE

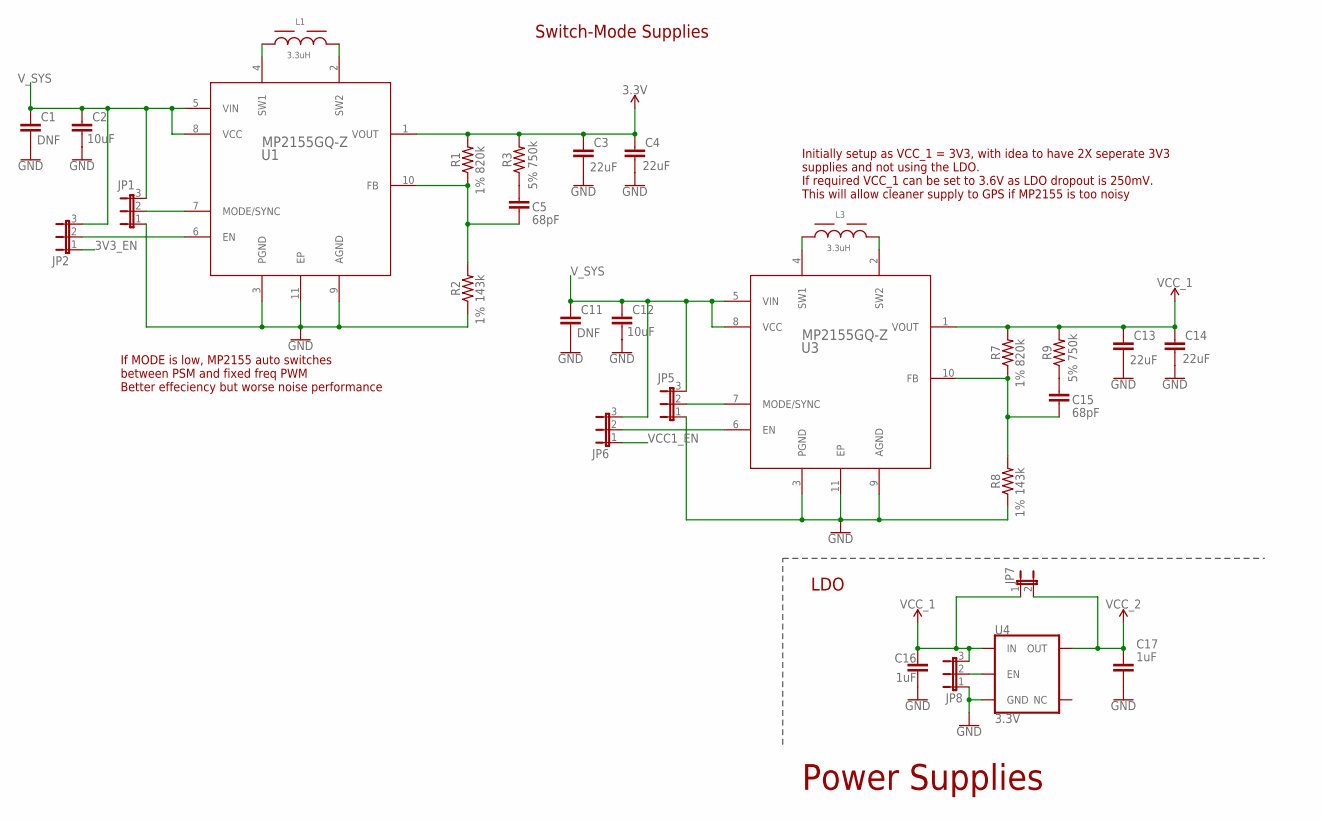
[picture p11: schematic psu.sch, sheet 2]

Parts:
C1, C11: DNF; CAPC2012X110
C2, C12: 10uF; CAPC2012X110; VOLTAGE_RATING 6.3V
C3, C4, C13, C14: 22uF; CAPC2012X110; VOLTAGE_RATING 10V
C5, C15: 68pF; CAPC1608X85; VOLTAGE_RATING 50V
C16, C17: 1uF; CAPC2012X110
JP1, JP2, JP5, JP6, JP8: JP2E; JP2
JP7: JP1E; JP1
L1, L3: 3.3uH; WE-HCI_7050
R1, R7: 820k; 0603; TOLERANCE 1%
R2, R8: 143k; 0603; TOLERANCE 1%
R3, R9: 750k; 0603; TOLERANCE 5%
U1, U3: MP2155GQ-Z; QFN-10_MP2155_MNP
U4: 3.3V; SOT23-5

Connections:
3.3V: C3.1, C4.1, R1.2, R3.2, U1.1 (VOUT); also elsewhere on the board
3V3_EN: JP2.1
GND: C1.2, C2.2, C3.2, C4.2, C11.2, C12.2, C13.2, C14.2, C16.2, C17.2, JP1.1, JP5.1, JP8.1, R2.1, R8.1, U1.3 (PGND), U1.9 (AGND), U1.11 (EP), U3.3 (PGND), U3.9 (AGND), U3.11 (EP), U4.2 (GND); also elsewhere on the board
unnamed: C5.1, R3.1
unnamed: JP1.2, U1.7 (MODE/SYNC)
unnamed: C5.2, R1.1, R2.2, U1.10 (FB)
unnamed: JP2.2, U1.6 (EN)
unnamed: L1.1, U1.4 (SW1)
unnamed: L1.2, U1.2 (SW2)
unnamed: JP5.2, U3.7 (MODE/SYNC)
unnamed: JP6.2, U3.6 (EN)
unnamed: C15.2, R7.1, R8.2, U3.10 (FB)
unnamed: C15.1, R9.1
unnamed: L3.1, U3.4 (SW1)
unnamed: L3.2, U3.2 (SW2)
unnamed: JP8.2, U4.3 (EN)
VCC1_EN: JP6.1
VCC_1: C13.1, C14.1, C16.1, JP7.1, JP8.3, R7.2, R9.2, U3.1 (VOUT), U4.1 (IN); also elsewhere on the board
VCC_2: C17.1, JP7.2, U4.5 (OUT); also elsewhere on the board
V_SYS: C1.1, C2.1, C11.1, C12.1, JP1.3, JP2.3, JP5.3, JP6.3, U1.5 (VIN), U1.8 (VCC), U3.5 (VIN), U3.8 (VCC); also elsewhere on the board

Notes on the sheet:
Initially setup as VCC_1 = 3V3, with idea to have 2X seperate 3V3 supplies and not using the LDO. If required VCC_1 can be set to 3.6V as LDO dropout is 250mV. This will allow cleaner supply to GPS if MP2155 is too noisy
Power Supplies
If MODE is low, MP2155 auto switches between PSM and fixed freq PWM Better effeciency but worse noise performance
LDO
Switch-Mode Supplies

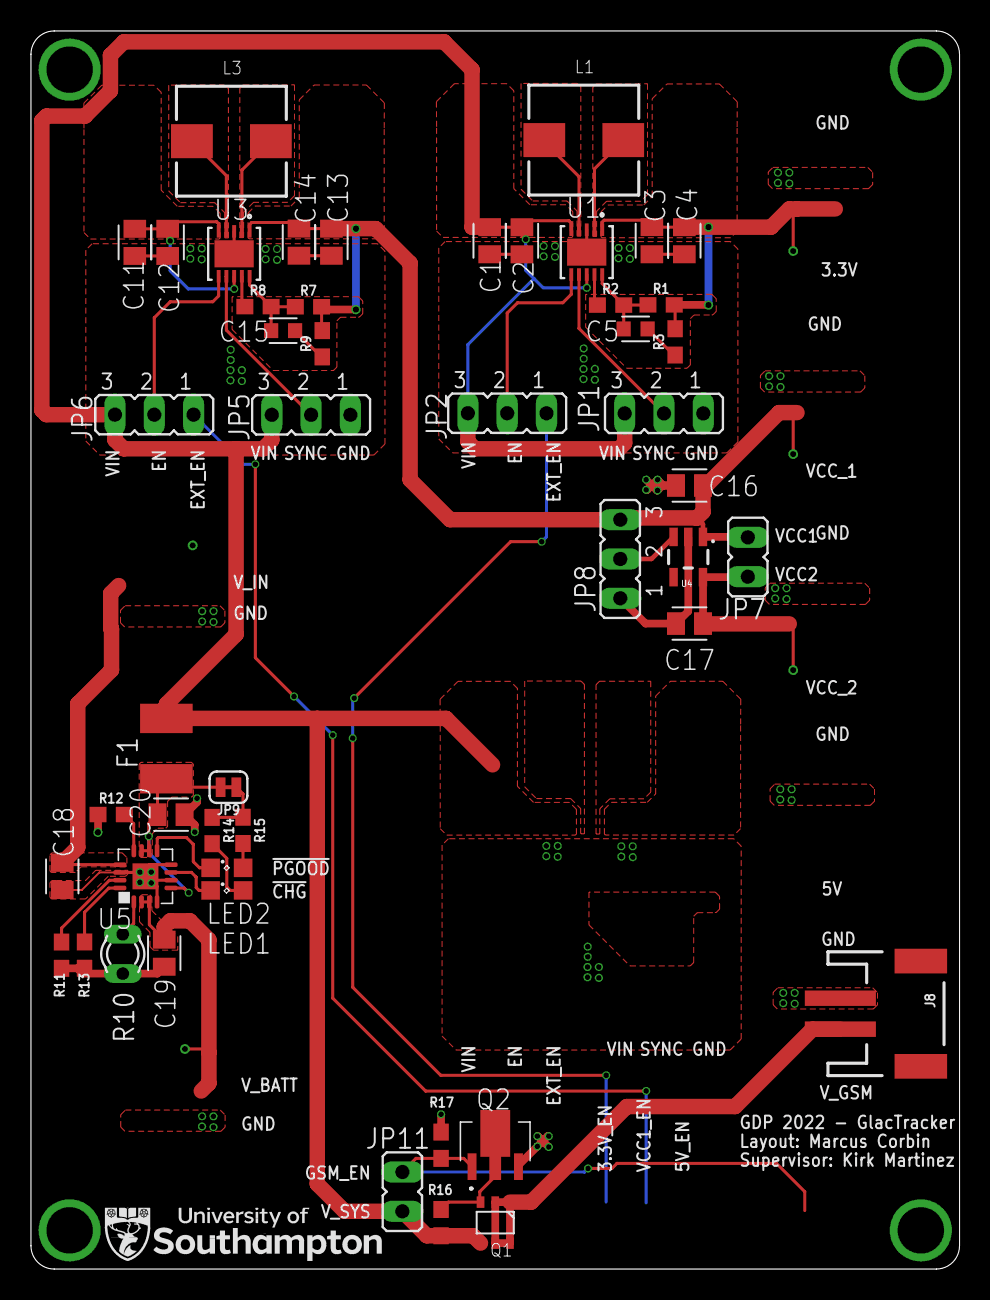
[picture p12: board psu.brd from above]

Board: 2 copper layers, 60.0 x 80.0 mm, 54 parts (0 on the bottom side), 33 nets.

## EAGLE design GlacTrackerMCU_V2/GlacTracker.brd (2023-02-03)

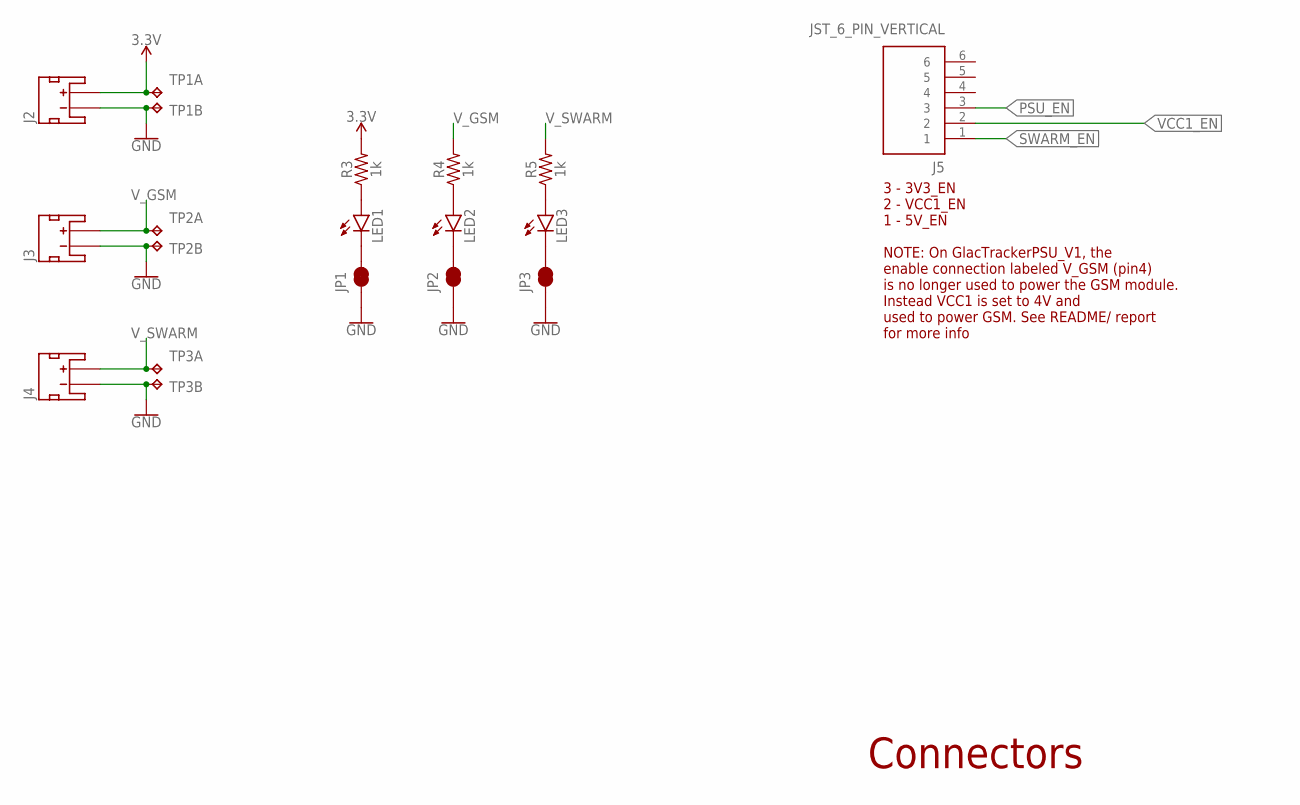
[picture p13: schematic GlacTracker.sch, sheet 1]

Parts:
J2, J3, J4: JST_2MM_MALE; JST-2-SMD
J5: JST_6_PIN_VERTICAL; JST-6-SMD-VERT-1.0MM
JP1, JP2, JP3: JUMPER-SMT_2_NC_TRACE_SILK; SMT-JUMPER_2_NC_TRACE_SILK
LED1, LED2, LED3: LEDCHIP-LED0805; CHIP-LED0805
R3, R4, R5: 1k; 0603
TP1, TP2, TP3: TP2P2-38-17; P2-38-17

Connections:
3.3V: J2.2 (+), R3.2, TP1.TP-1; also elsewhere on the board
GND: J2.1 (-), J3.1 (-), J4.1 (-), JP1.1, JP2.1, JP3.1, TP1.TP-2, TP2.TP-2, TP3.TP-2; also elsewhere on the board
unnamed: JP1.2, LED1.C
unnamed: JP2.2, LED2.C
unnamed: JP3.2, LED3.C
unnamed: LED1.A, R3.1
unnamed: LED2.A, R4.1
unnamed: LED3.A, R5.1
PSU_EN: J5.3; also elsewhere on the board
SWARM_EN: J5.1; also elsewhere on the board
VCC1_EN: J5.2; also elsewhere on the board
V_GSM: J3.2 (+), R4.2, TP2.TP-1; also elsewhere on the board
V_SWARM: J4.2 (+), R5.2, TP3.TP-1; also elsewhere on the board

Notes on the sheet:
Connectors
3 - 3V3_EN 2 - VCC1_EN 1 - 5V_EN NOTE: On GlacTrackerPSU_V1, the enable connection labeled V_GSM (pin4) is no longer used to power the GSM module. Instead VCC1 is set to 4V and used to power GSM. See README/ report for more info

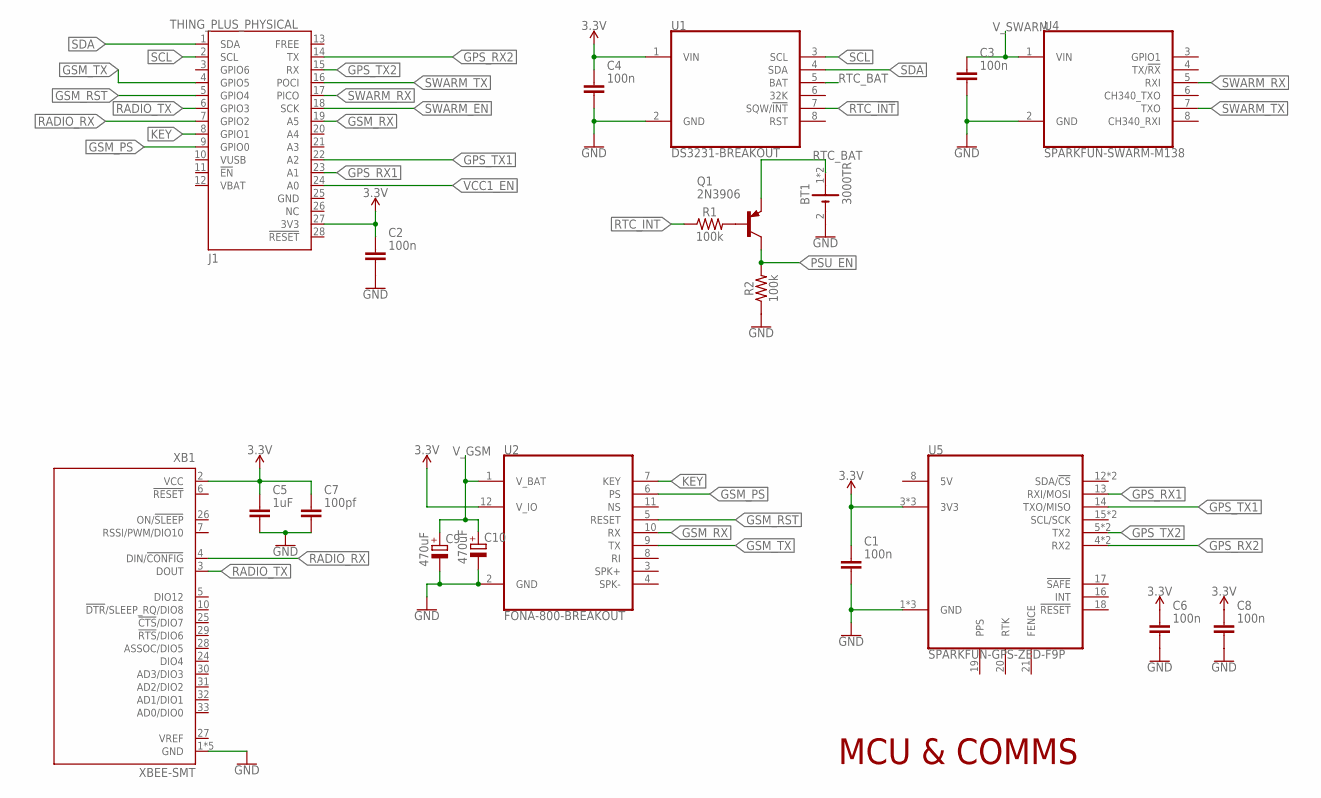
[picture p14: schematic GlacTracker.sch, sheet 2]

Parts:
BT1: 3000TR; BAT_3000TR
C1, C2, C3, C4, C6, C8: 100n; CAPC1608X85
C5: 1uF; CAPC1608X85
C7: 100pf; CAPC1608X85
C9, C10: 470uF; CAPPRD508W65D1000H1100B
J1: THING_PLUS_PHYSICAL; THING_PLUS
Q1: 2N3906; TO92
R1, R2: 100k; 0603
U1: DS3231-BREAKOUT
U2: FONA-800-BREAKOUT
U4: SPARKFUN-SWARM-M138
U5: SPARKFUN-GPS-ZED-F9P
XB1: XBEE-SMT

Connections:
3.3V: C1.1, C2.1, C4.1, C5.1, C6.1, C7.1, C8.1, J1.27 (3V3), U1.1 (VIN), U2.12 (V_IO), U5.3 (3V3), U5.9 (3V3), U5.24 (3V3), XB1.2 (VCC); also elsewhere on the board
GND: BT1.2 (-), C1.2, C2.2, C3.2, C4.2, C5.2, C6.2, C7.2, C8.2, C9.2 (-), C10.2 (-), R2.1, U1.2 (GND), U2.2 (GND), U4.2 (GND), U5.1 (GND), U5.7 (GND), U5.25 (GND), XB1.1 (GND), XB1.11 (GND), XB1.13 (GND), XB1.22 (GND), XB1.35 (GND); also elsewhere on the board
GPS_RX1: J1.23 (A1), U5.13 (RXI/MOSI)
GPS_RX2: J1.14 (TX), U5.4 (RX2), U5.11 (RX2)
GPS_TX1: J1.22 (A2), U5.14 (TXO/MISO)
GPS_TX2: J1.15 (RX), U5.5 (TX2), U5.10 (TX2)
GSM_PS: J1.9 (GPIO0), U2.6 (PS)
GSM_RST: J1.5 (GPIO4), U2.5 (RESET)
GSM_RX: J1.19 (A5), U2.10 (RX)
GSM_TX: J1.4 (GPIO5), U2.9 (TX)
KEY: J1.8 (GPIO1), U2.7 (KEY)
unnamed: Q1.2 (B), R1.2
PSU_EN: Q1.1 (C), R2.2; also elsewhere on the board
RADIO_RX: J1.7 (GPIO2), XB1.4 (DIN/!CONFIG)
RADIO_TX: J1.6 (GPIO3), XB1.3 (DOUT)
RTC_!INT: R1.1, U1.7 (SQW/!INT)
RTC_BAT: BT1.1 (+), BT1.3 (+), Q1.3 (E), U1.5 (BAT)
SCL: J1.2 (SCL), U1.3 (SCL)
SDA: J1.1 (SDA), U1.4 (SDA)
SWARM_EN: J1.18 (SCK); also elsewhere on the board
SWARM_RX: J1.17 (PICO), U4.5 (RXI)
SWARM_TX: J1.16 (POCI), U4.7 (TXO)
VCC1_EN: J1.24 (A0); also elsewhere on the board
V_GSM: C9.1 (+), C10.1 (+), U2.1 (V_BAT); also elsewhere on the board
V_SWARM: C3.1, U4.1 (VIN); also elsewhere on the board

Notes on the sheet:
MCU & COMMS

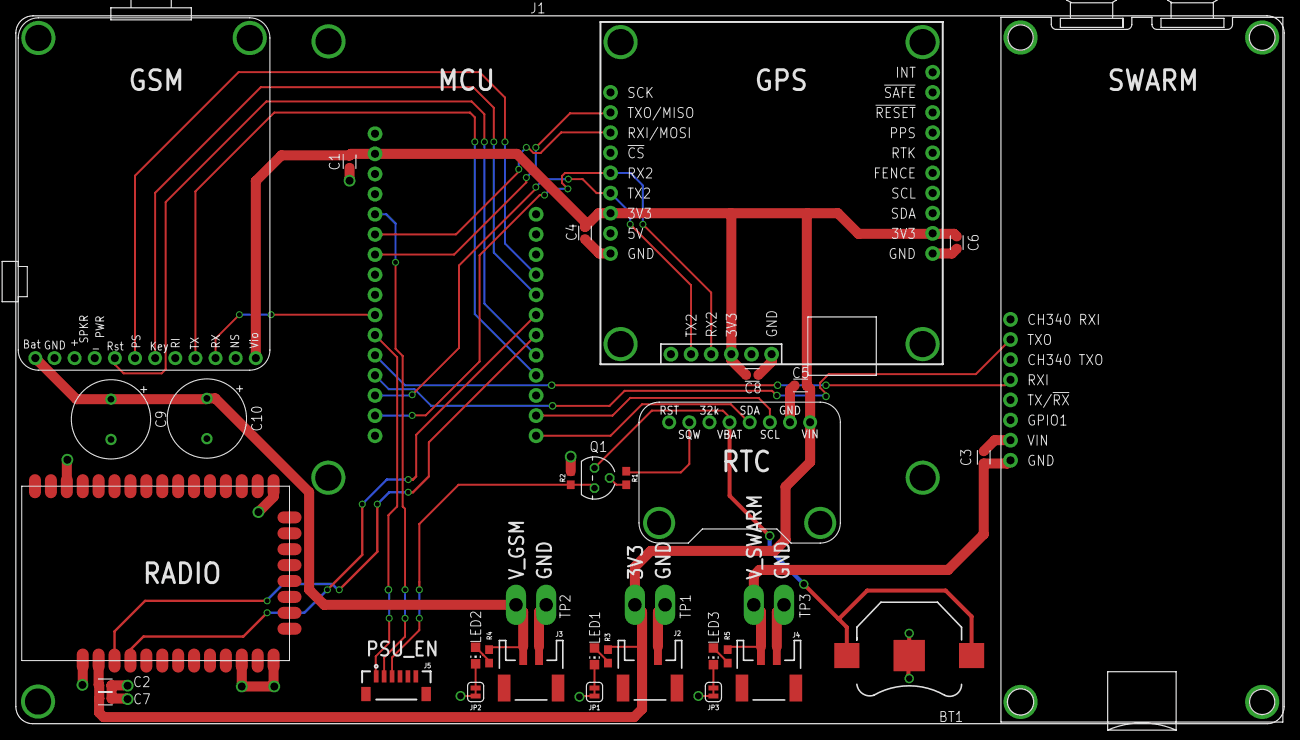
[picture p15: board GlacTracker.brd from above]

Board: 2 copper layers, 160.0 x 89.3 mm, 36 parts (0 on the bottom side), 31 nets.

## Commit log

2023-04-12 add Eagle git ignore, add initial progress on the combined board
    [tracker.brd, tracker.sch]
2023-04-17 Complete board for checking and naming
    [tracker.brd, tracker.sch]
2023-04-17 added a break line
    [tracker.brd]
2023-04-18 pre-tweak commt
    [tracker.brd]
2023-04-18 DRCand ERC run. Some tweaks to make to the Swarm/GSMoverlap
    [tracker.brd, tracker.sch]
2023-04-18 missed and airwire
    [tracker.brd, tracker.sch]
2023-04-19 track tweak
    [tracker.brd]
2023-04-19 Add a logo
    [tracker.brd]
2023-04-19 Added accelerometer
    [tracker.brd, tracker.sch]
2023-04-20 Change Key to be grounded and add an Admin pinheader for a button
    [tracker.brd, tracker.sch]
2023-04-21 Fix the overlapping holes DRC
    [tracker.brd, tracker.sch]
2023-04-21 Add BatVolts divider values
    [tracker.brd, tracker.sch]
2023-04-21 update the silkscreen
    [tracker.brd]
2023-04-25 Rename to IT3
    [psu.brd, psu.sch, tracker.brd, tracker.sch]
2023-04-25 Added Eagle 9 version
    [tracker-Eagle9.brd, tracker-Eagle9.sch]
2023-04-25 Firx DRC issues in Eagle 9
    [tracker-Eagle9.brd]
2023-04-25 Final silkscreen tweaks and generation of production files
    [tracker-Eagle9.brd, tracker-Eagle9.sch, tracker-Eagle9_bom.csv, tracker-Eagle9_cpl.csv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]
2023-04-26 Tweaks to PCB, BOM and CPL for production. Should be ready to run
    [tracker-Eagle9.brd, tracker-Eagle9_bom.csv, tracker-Eagle9_cpl.csv, tracker.brd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]
2023-05-02 Update 4V PSUvalues
    [tracker-Eagle9.brd, tracker-Eagle9.sch, tracker-Eagle9_bom.csv, tracker.brd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]
2023-05-26 Fixes for accelerometer CS pullup
    [tracker-Eagle9.brd, tracker-Eagle9.sch, tracker.brd, tracker.sch]
2023-06-23 Properly fix the accelerometer issue and move the GPS power FET slightly
    [tracker.brd, tracker.sch]

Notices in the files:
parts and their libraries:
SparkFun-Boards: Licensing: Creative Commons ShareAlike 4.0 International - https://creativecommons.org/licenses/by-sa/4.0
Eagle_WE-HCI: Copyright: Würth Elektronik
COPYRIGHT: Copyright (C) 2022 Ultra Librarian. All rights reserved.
